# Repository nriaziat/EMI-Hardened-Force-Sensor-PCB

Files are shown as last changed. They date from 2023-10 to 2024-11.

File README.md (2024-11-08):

# EMI Hardened Force Sensor PCB

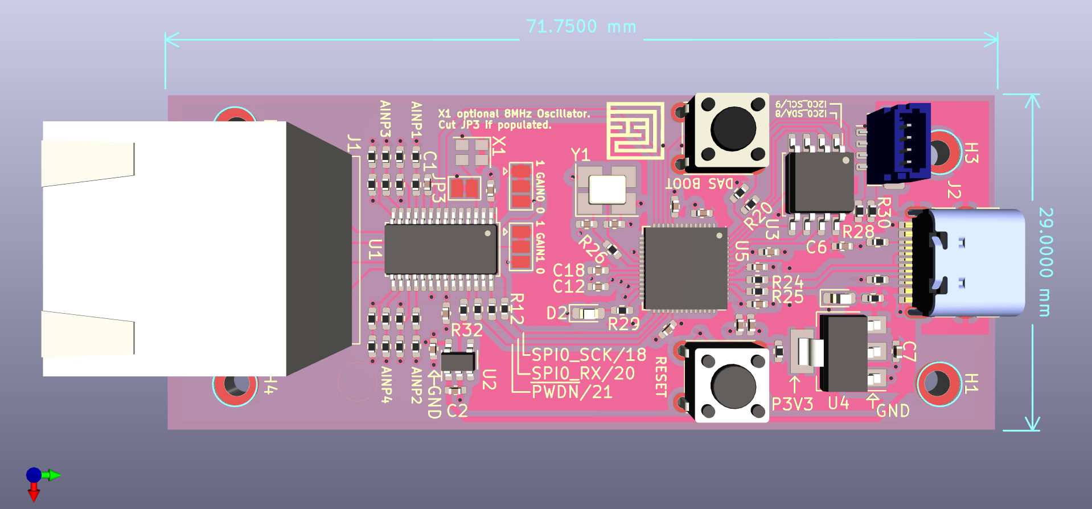
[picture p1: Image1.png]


<!--- This template should be used if the project contains hardware designs. If the project contains both hardware and software designs, please also refer to software-readme-template.md and incorporate relevant sections. -->

## Contents

<!---List file contents of the project, in table.--->

| File/folder | Description |
|-------------|-------------|
| `MazeStrainGaugeAmplifier.pdf`       | Schematic |
| `ibom.html`       | Bill of materials |
| `PCB.pdf`        | Report on PCB stack-up |
| `README.md` | This README file. |
| `LICENSE`   | The license for the project. |

## Design Tools

* KiCAD 6.0

## Key concepts

For more information about this project, please refer to our publication: [Riaziat, Naveed D., et al. "Investigating Haptic Feedback in Vision-Deficient Millirobot Telemanipulation." IEEE Robotics and Automation Letters (2024)](https://ieeexplore.ieee.org/abstract/document/10521760/).
Designed for use with the Texas Measurment [QMFLA-5-350-11-1LJAY-F](https://tml.jp/e/product/strain_gauge/mf_list.html) and the [RP2040](https://www.raspberrypi.com/products/rp2040/).
For maximum EMI resistance, we reccommend using twisted and shielded cabling as well as the included 3D printed housing with copper tape lining. 

## Project expectations

* The design has been manufactured and tested. Board was ordered through OSH Park and hand assembled.

### Expected support for the project

<!---If you will reply to issues, please suggest how users should report problems or reach out. Github issues is preferable.--->

* Will attempt reply to Github Issues with no guarantee.
* Project is provided without any support. 

## License

For details on license, see LICENSE in this directory.

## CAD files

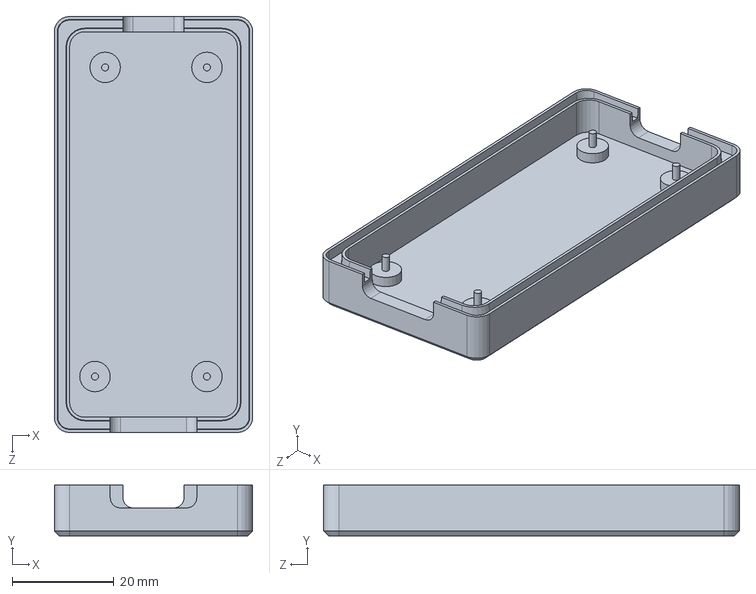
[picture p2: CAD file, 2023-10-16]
case.SLDPRT
39.0 x 10.0 x 81.8 mm

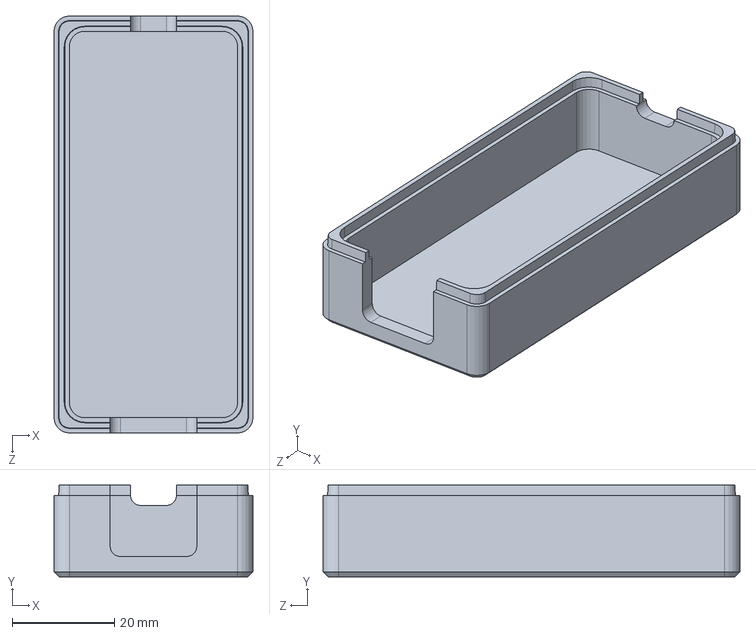
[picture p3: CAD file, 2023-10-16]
case_top.SLDPRT
39.0 x 18.0 x 81.8 mm

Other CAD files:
case.STL
case_top.STL

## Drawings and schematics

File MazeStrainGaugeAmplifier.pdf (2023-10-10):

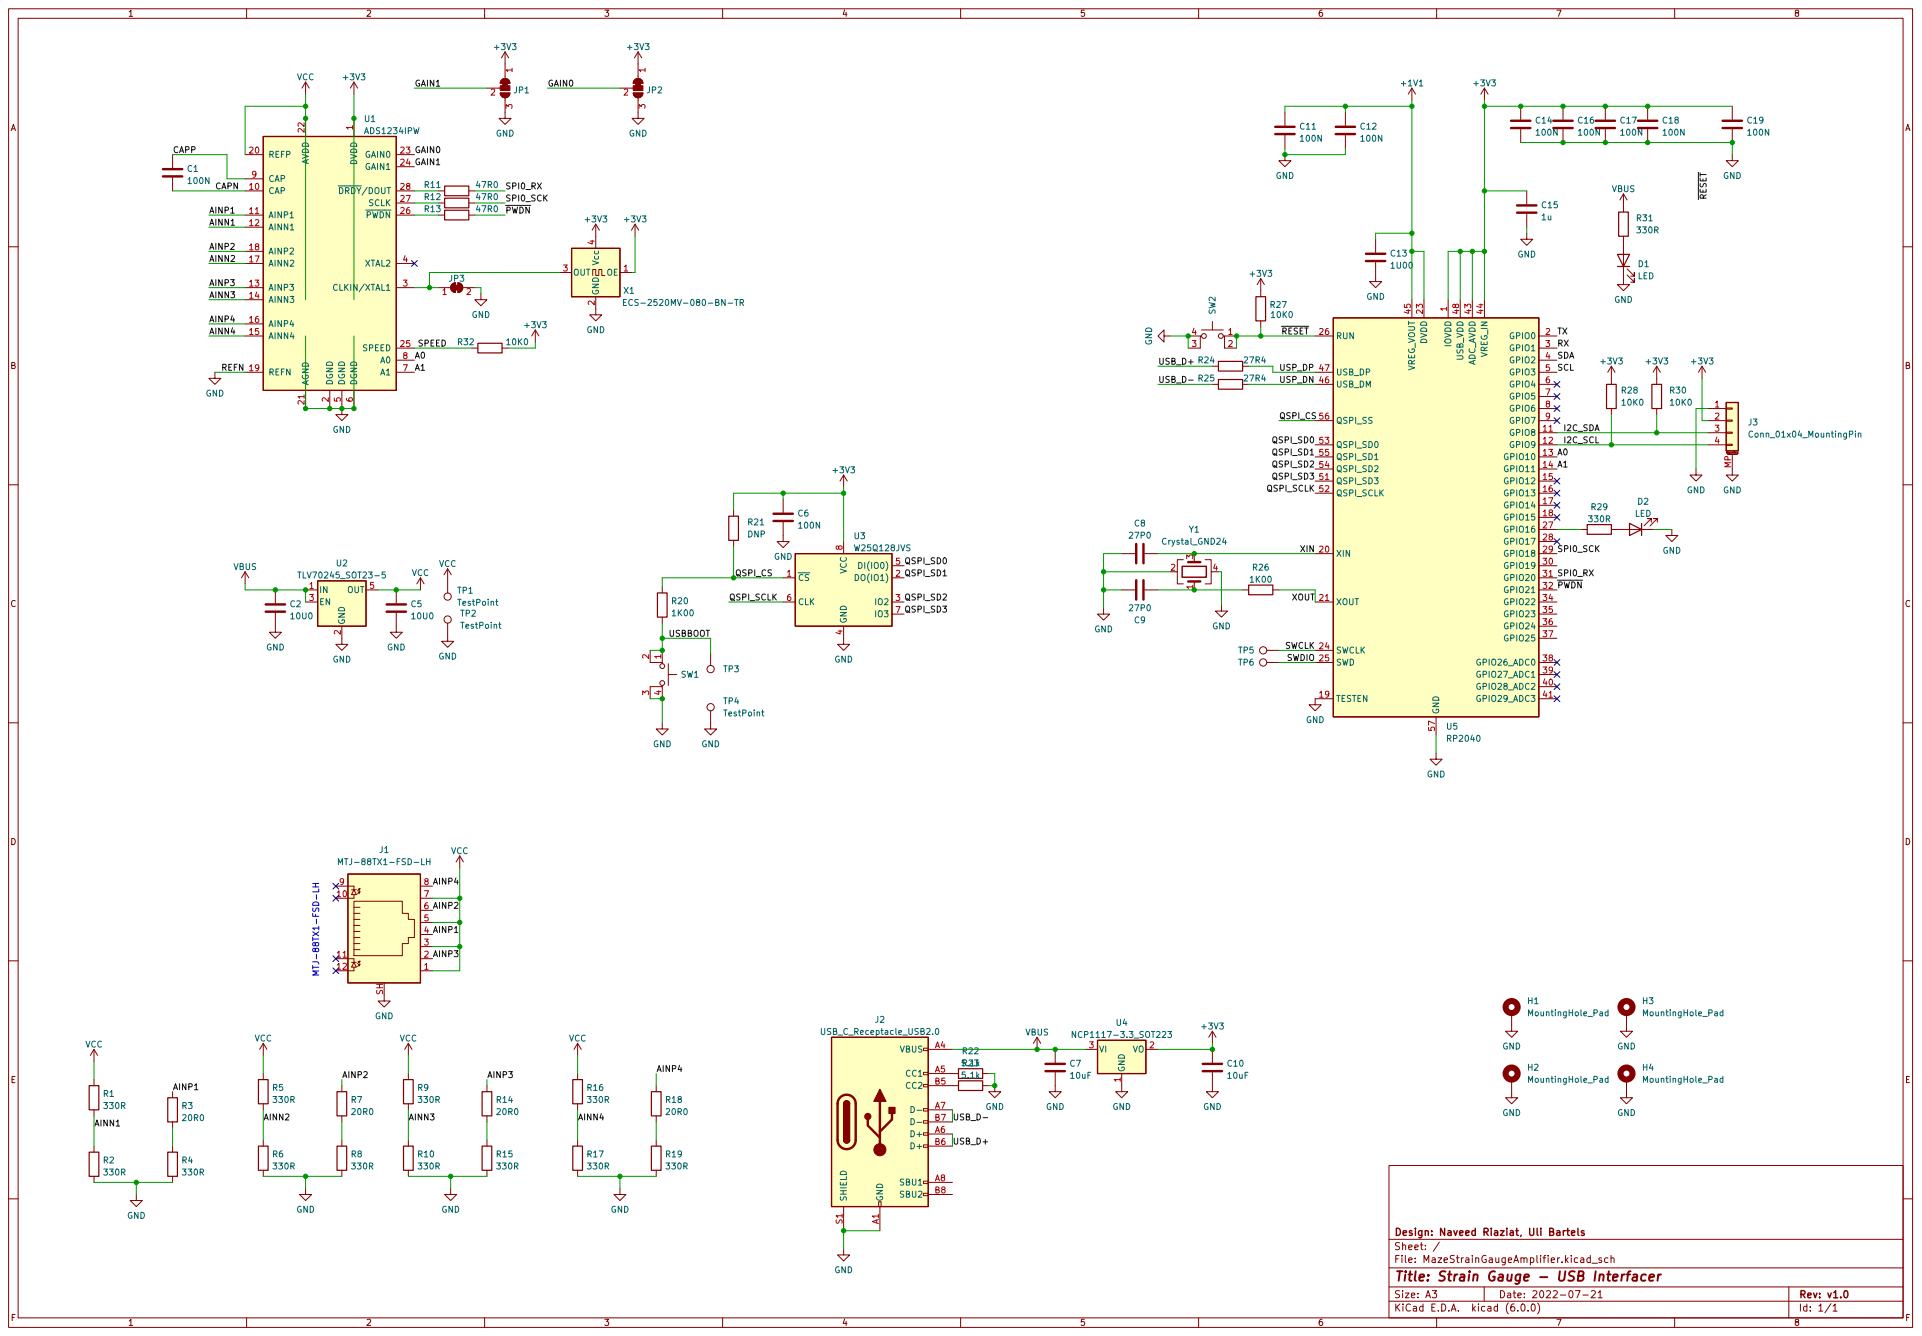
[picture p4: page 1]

2 REFP 20 AGND 21 AVDD 22 GAIN0 23 GAIN1 24 SPEED 25 ~{PWDN} 26 SCLK 27 ~{DRDY}/DOUT 28 CLKIN/XTAL1 3 XTAL2 4 DGND

2 OUT 3 Vcc 4 X1ECS-2520MV-080-BN-TR

1 GPIO8 11 GPIO9 12 GPIO10 13 GPIO11 14 GPIO12 15 GPIO13 16 GPIO14 17 GPIO15 18 TESTEN 19 GPIO0 2 XIN 20 XOUT 21 DVDD 23 SWCLK 24 SWD 25 RUN 26 GPIO16 27 GPIO17 28 GPIO18 29 GPIO1 3 GPIO19 30 GPIO20 31 GPIO21 32 GPIO22 34 GPIO23 35 GPIO24 36 GPIO25 37 GPIO26_ADC0 38 GPIO27_ADC1 39 GPIO2 4 GPIO28_ADC2 40 GPIO29_ADC3 41 ADC_AVDD 43 VREG_IN 44 VREG_VOUT 45 USB_DM 46 USB_DP 47 USB_VDD 48 GPIO3 5 QSPI_SD3 51 QSPI_SCLK 52 QSPI_SD0 53 QSPI_SD2 54 QSPI_SD1 55 QSPI_SS 56 GND 57 GPIO4 6 GPIO5 7 GPIO6 8 GPIO7 9 U5RP2040

File: MazeStrainGaugeAmplifier.kicad_sch Sheet: / Design: Naveed Riaziat, Uli Bartels

Id: 1/1 Title: Strain Gauge - USB Interfacer

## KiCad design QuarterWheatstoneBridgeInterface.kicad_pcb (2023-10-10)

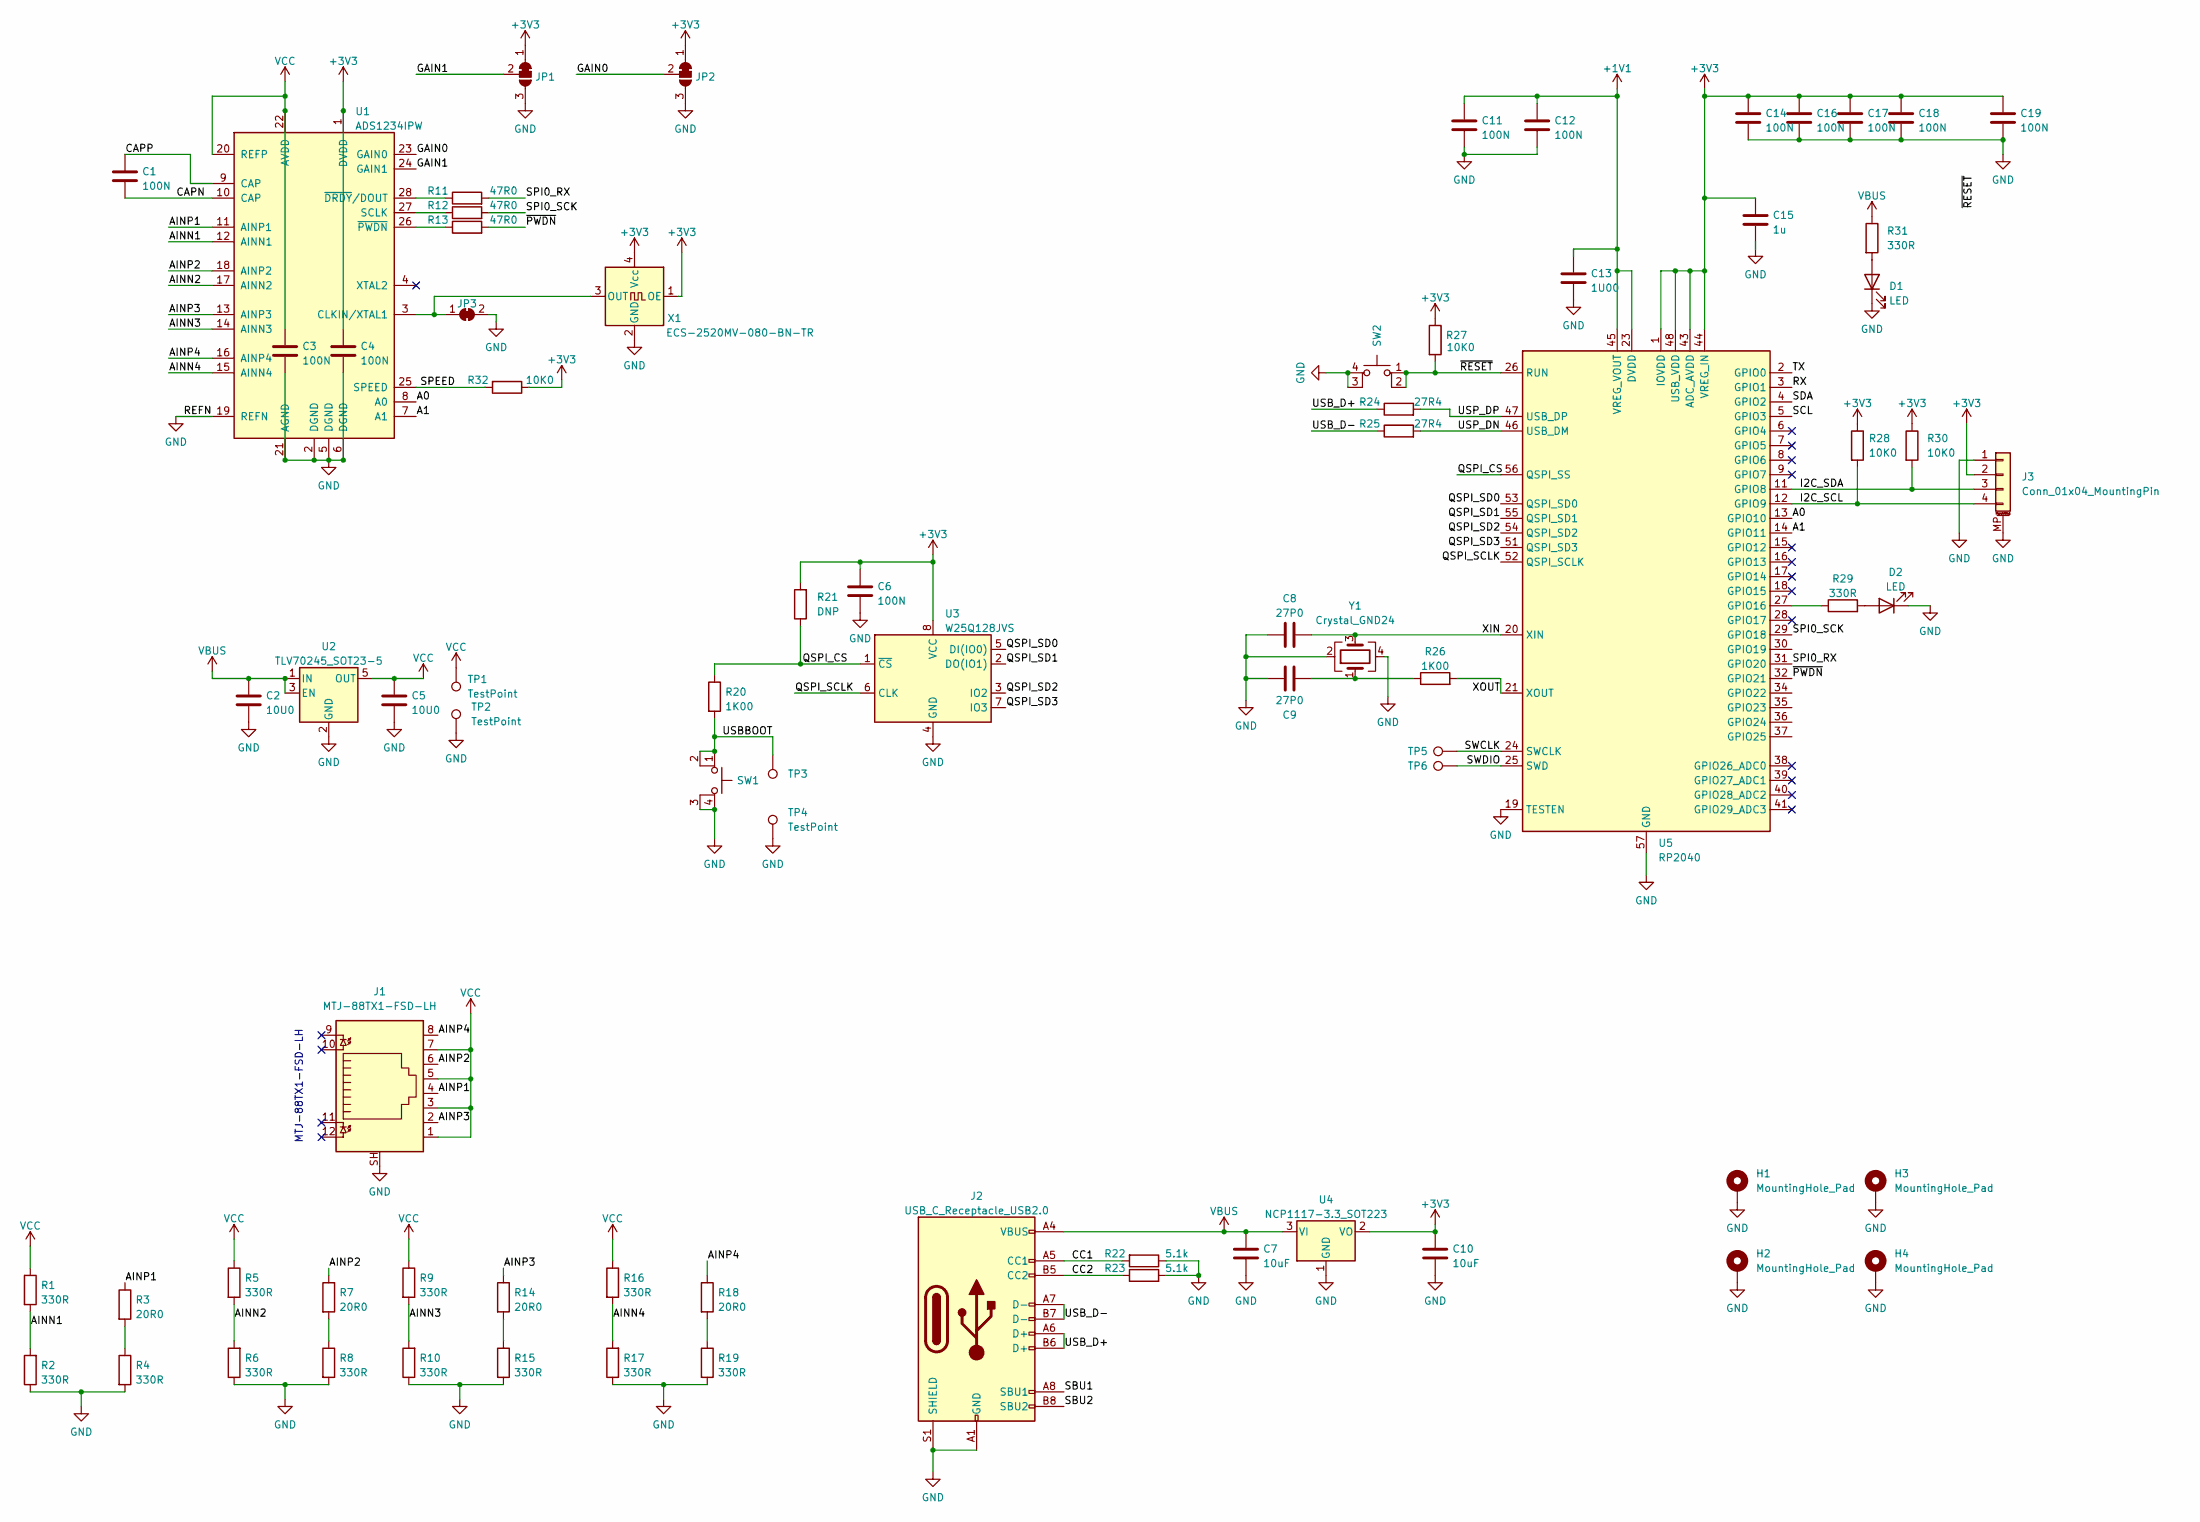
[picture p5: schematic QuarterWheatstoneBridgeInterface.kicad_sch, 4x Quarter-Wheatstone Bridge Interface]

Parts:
C1, C3, C4, C6, C11, C12, C14, C16, C17, C18, C19: 100N; C_0402_1005Metric_Pad0.74x0.62mm_HandSolder
C2, C5: 10U0; C_0402_1005Metric_Pad0.74x0.62mm_HandSolder
C7, C10: 10uF; C_0402_1005Metric_Pad0.74x0.62mm_HandSolder
C8, C9: 27P0; C_0402_1005Metric_Pad0.74x0.62mm_HandSolder
C13: 1U00; C_0402_1005Metric_Pad0.74x0.62mm_HandSolder
C15: 1u; C_0402_1005Metric_Pad0.74x0.62mm_HandSolder
D1, D2: LED; LED_0603_1608Metric_Pad1.05x0.95mm_HandSolder
H1, H2, H3, H4: MountingHole_Pad; MountingHole_2.2mm_M2_DIN965_Pad
J1: MTJ-88TX1-FSD-LH; RJ45_Hanrun_HR911105A
J2: USB_C_Receptacle_USB2.0; USB_C_Receptacle_HRO_TYPE-C-31-M-12
J3: Conn_01x04_MountingPin; JST_SH_BM04B-SRSS-TB_1x04-1MP_P1.00mm_Vertical
JP1, JP2: SolderJumper_3_Bridged12; SolderJumper-3_P1.3mm_Bridged12_Pad1.0x1.5mm
JP3: SolderJumper_2_Bridged; SolderJumper-2_P1.3mm_Bridged_Pad1.0x1.5mm
R1, R2, R4, R5, R6, R8, R9, R10, R15, R16, R17, R19, R29, R31: 330R; R_0402_1005Metric_Pad0.72x0.64mm_HandSolder
R3, R7, R14, R18: 20R0; R_0402_1005Metric_Pad0.72x0.64mm_HandSolder
R11, R12, R13: 47R0; R_0402_1005Metric_Pad0.72x0.64mm_HandSolder
R20, R26: 1K00; R_0402_1005Metric_Pad0.72x0.64mm_HandSolder
R21: DNP; R_0402_1005Metric_Pad0.72x0.64mm_HandSolder
R22, R23: 5.1k; R_0402_1005Metric_Pad0.72x0.64mm_HandSolder
R24, R25: 27R4; R_0402_1005Metric_Pad0.72x0.64mm_HandSolder
R27, R28, R30, R32: 10K0; R_0402_1005Metric_Pad0.72x0.64mm_HandSolder
SW1, SW2: SW_MEC_5E; SW_TH_Tactile_Omron_B3F-10xx
TP1, TP2, TP4: TestPoint; TestPoint_Pad_D3.0mm
TP3, TP5, TP6: TestPoint; TestPoint_Pad_D4.0mm
U1: ADS1234IPW; TSSOP-28_4.4x9.7mm_P0.65mm
U2: TLV70245_SOT23-5; SOT-23-5
U3: W25Q128JVS; SOIC-8_5.23x5.23mm_P1.27mm
U4: NCP1117-3.3_SOT223; SOT-223-3_TabPin2
U5: RP2040; QFN-56-1EP_7x7mm_P0.4mm_EP3.2x3.2mm
X1: ECS-2520MV-080-BN-TR; Oscillator_SMD_SeikoEpson_SG210-4Pin_2.5x2.0mm
Y1: Crystal_GND24; Crystal_SMD_3225-4Pin_3.2x2.5mm_HandSoldering

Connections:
+1V1: C11.1, C12.1, C13.1, U5.23 (DVDD), U5.45 (VREG_VOUT), U5.50 (DVDD)
+3V3: C4.1, C6.1, C10.1, C14.1, C15.1, C16.1, C17.1, C18.1, C19.1, J3.2, JP1.1 (A), JP2.1 (A), R21.2, R27.1, R28.1, R30.1, R32.1, U1.1 (DVDD), U3.8 (VCC), U4.2 (VO), U5.1 (IOVDD), U5.10 (IOVDD), U5.22 (IOVDD), U5.33 (IOVDD), U5.42 (IOVDD), U5.43 (ADC_AVDD), U5.44 (VREG_IN), U5.48 (USB_VDD), U5.49 (IOVDD), X1.1 (OE), X1.4 (Vcc)
/A0: U1.8 (A0), U5.13 (GPIO10)
/A1: U1.7 (A1), U5.14 (GPIO11)
/AINN1: R1.2, R2.2, U1.12 (AINN1)
/AINN2: R5.2, R6.2, U1.17 (AINN2)
/AINN3: R9.2, R10.2, U1.14 (AINN3)
/AINN4: R16.2, R17.2, U1.15 (AINN4)
/AINP1: J1.4, R3.1, U1.11 (AINP1)
/AINP2: J1.6, R7.1, U1.18 (AINP2)
/AINP3: J1.2, R14.1, U1.13 (AINP3)
/AINP4: J1.8, R18.1, U1.16 (AINP4)
/CAPN: C1.2, U1.10 (CAP)
/CAPP: C1.1, U1.9 (CAP)
/CC1: J2.A5 (CC1), R22.2
/CC2: J2.B5 (CC2), R23.1
/GAIN0: JP2.2 (C), U1.23 (GAIN0)
/GAIN1: JP1.2 (C), U1.24 (GAIN1)
/I2C_SCL: J3.4, R28.2, U5.12 (GPIO9)
/I2C_SDA: J3.3, R30.2, U5.11 (GPIO8)
/QSPI_CS: R20.1, R21.1, U3.1 (~CS), U5.56 (QSPI_SS)
/QSPI_SCLK: U3.6 (CLK), U5.52 (QSPI_SCLK)
/QSPI_SD0: U3.5 (DI(IO0)), U5.53 (QSPI_SD0)
/QSPI_SD1: U3.2 (DO(IO1)), U5.55 (QSPI_SD1)
/QSPI_SD2: U3.3 (IO2), U5.54 (QSPI_SD2)
/QSPI_SD3: U3.7 (IO3), U5.51 (QSPI_SD3)
/RX: U5.3 (GPIO1)
/SBU1: J2.A8 (SBU1)
/SBU2: J2.B8 (SBU2)
/SCL: U5.5 (GPIO3)
/SDA: U5.4 (GPIO2)
/SPEED: R32.2, U1.25 (SPEED)
/SPI0_RX: R11.2, U5.31 (GPIO20)
/SPI0_SCK: R12.2, U5.29 (GPIO18)
/SWCLK: TP5.1, U5.24 (SWCLK)
/SWDIO: TP6.1, U5.25 (SWD)
/TX: U5.2 (GPIO0)
/USBBOOT: R20.2, SW1.1, SW1.2, TP3.1
/USB_D+: J2.A6 (D+), J2.B6 (D+), R24.1
/USB_D-: J2.A7 (D-), J2.B7 (D-), R25.1
/USP_DN: R25.2, U5.46 (USB_DM)
/USP_DP: R24.2, U5.47 (USB_DP)
/XIN: C8.2, U5.20 (XIN), Y1.3
/XOUT: R26.2, U5.21 (XOUT)
/~PWDN: R13.2, U5.32 (GPIO21)
/~RESET: R27.2, SW2.1, SW2.2, U5.26 (RUN)
GND: C2.2, C3.2, C4.2, C5.2, C6.2, C7.2, C8.1, C9.2, C10.2, C11.2, C12.2, C13.2, C14.2, C15.2, C16.2, C17.2, C18.2, C19.2, D1.1 (K), D2.1 (K), H1.1, H2.1, H3.1, H4.1, J1.SH, J2.A1 (GND), J2.A12 (GND), J2.B1 (GND), J2.B12 (GND), J2.S1 (SHIELD), J3.1, J3.MP (MountPin), JP1.3 (B), JP2.3 (B), JP3.2 (B), R2.1, R4.2, R6.1, R8.2, R10.1, R15.2, R17.1, R19.2, R22.1, R23.2, SW1.3 (K), SW1.4 (A), SW2.3 (K), SW2.4 (A), TP2.1, TP4.1, U1.2 (DGND), U1.5 (DGND), U1.6 (DGND), U1.19 (REFN), U1.21 (AGND), U2.2 (GND), U3.4 (GND), U4.1 (GND), U5.19 (TESTEN), U5.57 (GND), X1.2 (GND), Y1.2, Y1.4
unnamed: C9.1, R26.1, Y1.1
unnamed: D1.2 (A), R31.2
unnamed: D2.2 (A), R29.2
unnamed: JP3.1 (A), U1.3 (CLKIN/XTAL1), X1.3 (OUT)
unnamed: R3.2, R4.1
unnamed: R7.2, R8.1
unnamed: R11.1, U1.28 (~DRDY/DOUT)
unnamed: R12.1, U1.27 (SCLK)
unnamed: R13.1, U1.26 (~PWDN)
unnamed: R14.2, R15.1
unnamed: R18.2, R19.1
unnamed: R29.1, U5.27 (GPIO16)
VBUS: C2.1, C7.1, J2.A4 (VBUS), J2.A9 (VBUS), J2.B4 (VBUS), J2.B9 (VBUS), R31.1, U2.1 (IN), U2.3 (EN), U4.3 (VI)
VCC: C3.1, C5.1, J1.1, J1.3, J1.5, J1.7, R1.1, R5.1, R9.1, R16.1, TP1.1, U1.20 (REFP), U1.22 (AVDD), U2.5 (OUT)

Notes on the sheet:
MTJ-88TX1-FSD-LH

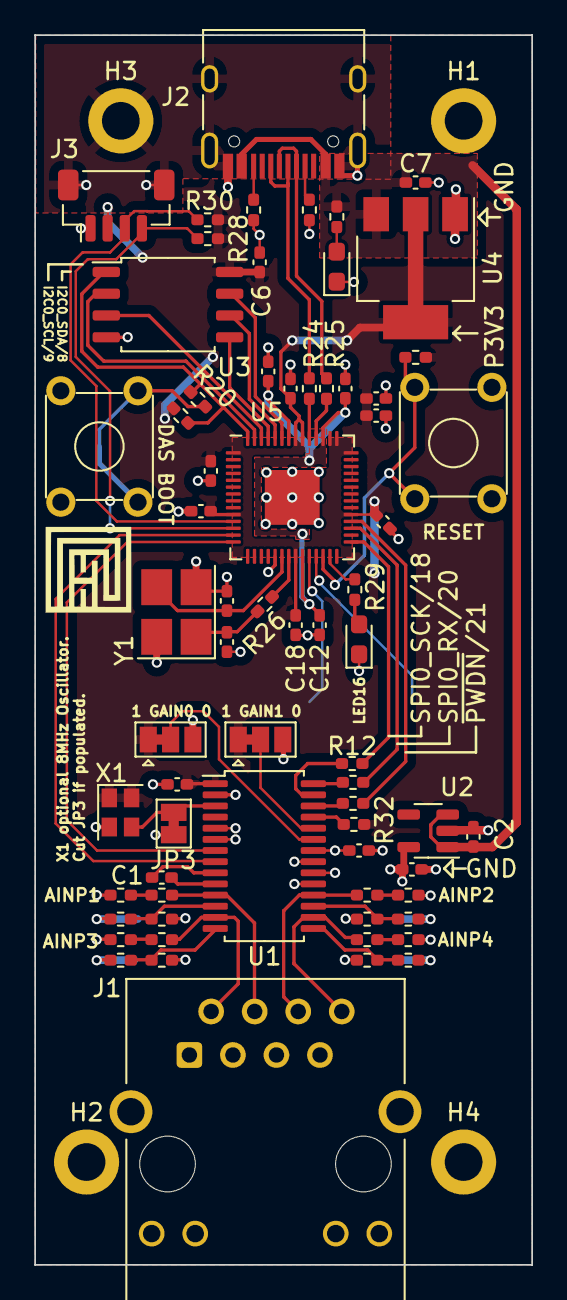
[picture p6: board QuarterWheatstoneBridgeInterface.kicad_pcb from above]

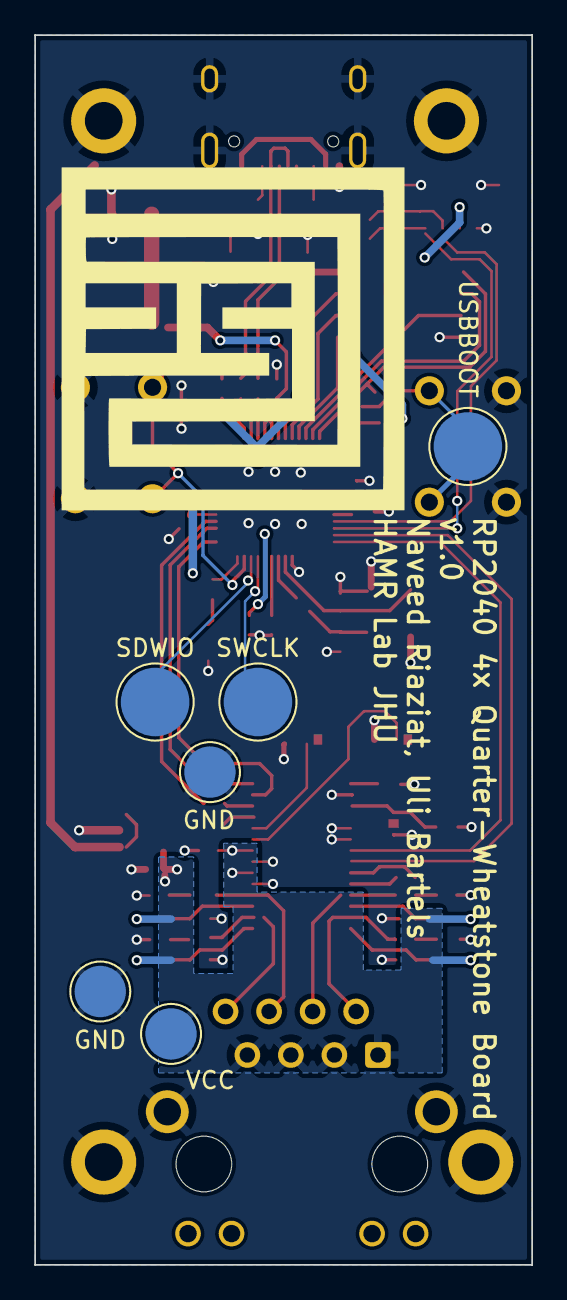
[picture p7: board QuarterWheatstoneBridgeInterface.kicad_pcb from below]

Board: 2 copper layers, 29.0 x 71.8 mm, 78 parts (6 on the bottom side), 55 nets.

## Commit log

2023-10-10 initial push
    [QuarterWheatstoneBridgeInterface.kicad_pcb, QuarterWheatstoneBridgeInterface.kicad_sch]
2023-10-16 add housing
    [case.SLDPRT, case_top.SLDPRT]
2023-10-16 add universal STL files
    [case.STL, case_top.STL]
